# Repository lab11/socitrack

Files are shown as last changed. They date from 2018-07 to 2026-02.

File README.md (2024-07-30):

TotTag
======

If you are interested in incorporating TotTag devices into your future
research, please fill out this [Interest Form](https://forms.gle/SqWca9DrKpcx9rBL6).

> **Note: This system is currently under heavy development. At the moment, it
> is provided as-is with no mechanism for external support, technical or
> otherwise.  In the future, once the project has reached a steady state and
> staffing has ramped up, we may begin providing limited support. We will post
> any updates on that front here. Thank you for your understanding!**

The TotTag is a self-contained PCB which utilizes a hybrid ultra wideband (UWB)
and Bluetooth Low Energy (BLE) radio design to enable high-fidelity interaction
tracking between devices _without_ requiring any supporting infrastructure.

<!--
- The SquarePoint module - 3 UWB antennas
- Nordic Semiconductors nRF52840 BLE radio
- 3.3V LDO designed to be used with 4.2V LiPo batteries
- Battery charge management controller
- SD card holder
- microUSB connector including FTDI FT232R for debugging
- 3-axis accelerometer
-->

TotTag saw a major plaform refresh in 2023 with a largely new hardware and
software design. Please bear with us as documentation and guidance throughout
this repositority updates to match the latest state of the TotTag project.

- [Documentation & Getting Started Guide](doc/)
- [Hardware details](hardware/)
- [Software details](software/)

History, Related Projects, & Relevant Publications
==================================================

This current effort builds on a long line of work exploring the capabilities of
ultra wideband under resource-constrained settings. This repository is an
evolution of projects exploring COTS-based solutions; some others linked below
explore more custom ultra wideband as well.

SociTrack and TotTag Gen 1
--------------------------

- Salo, V. C., Pannuto, P., Hedgecock, W., Biri, A., Russo, D. A., Piersiak, H. A., & Humphreys, K. L. (2022). Measuring naturalistic proximity as a window into caregiver-child interaction patterns. Behavior research methods, 54(4), 1580–1594. https://doi.org/10.3758/s13428-021-01681-8

- Andreas Biri, Neal Jackson, Lothar Thiele, Pat Pannuto, and Prabal Dutta. 2020.
*SociTrack: Infrastructure-Free Interaction Tracking through Mobile Sensor Networks.*
In The 26th Annual International Conference on Mobile Computing and Networking
(MobiCom ’20), September 21–25, 2020, London, United Kingdom. ACM, New York, NY,
USA, 14 pages. https://doi.org/10.1145/3372224.3419190

<!--
- Andreas Biri, Pat Pannuto, and Prabal Dutta. 2019.
*Demo Abstract: Tot-Ternary - A Wearable Platform for Social Interaction Tracking.*
In The 18th International Conference on Information Processing in Sensor Networks
(co-located with CPS-IoT Week 2019) (IPSN ’19), April 16-18, 2019, Montreal, QC,
Canada. ACM, New York, NY, USA, 2 pages. https://doi.org/10.1145/3302506.3312486
-->

<details>
<summary>Legacy documentation from SociTrack / TotTag Gen 1
</summary>

SociTrack
=========

*SociTrack* is a system for using ultra-wideband RF time-of-flight processing to
perform indoor ranging and localization. It incorporates the *SquarePoint*
module, containing a DecaWave DW1000 radio for UWB packet transmission and
timestamping. This module provides node-to-node ranges over an I<sup>2</sup>C
interface which can then be stored locally or transmitted externally.

Hardware
--------

The **SociTrack** system is composed of several hardware pieces. At its core is
the *SquarePoint* module, a 30mm x 15mm PCB that encompasses all of the
core ranging hardware and firmware. *SquarePoint* is provided as an EAGLE board
that allows for direct integration as a design block as part of the
[Lab11 EAGLE library](https://github.com/lab11/eagle). One example of a project
that uses the *SquarePoint* module is the *TotTag*, which comprises an
all-in-one tracking and localization system for mobile nodes. The *TotTag*
hardware includes three UWB antennas and a Bluetooth Low Energy (BLE) radio,
plus a battery charging circuit, SD card for data logging, accelerometer, USB
connectivity, and integrated sensor fusion. TotTag is able to provide ranges and
position estimates directly to a mobile phone application in real-time and can
be configured on-the-fly using a simple user interface over
[Summon](https://github.com/lab11/summon).

### SquarePoint

SquarePoint, an EAGLE design block for UWB ranging, includes the following
components:

- DecaWave DW1000 UWB radio
- STMicroelectronics STM32F091CCU6 MCU
- RF switch

The MCU contains all of the necessary code to control the DW1000 and run the
ranging protocol. This module provides a simple abstraction layer for quick
integration with a carrier board over an I<sup>2</sup>C interface without having
to worry about any underlying implementation details.

### TotTag

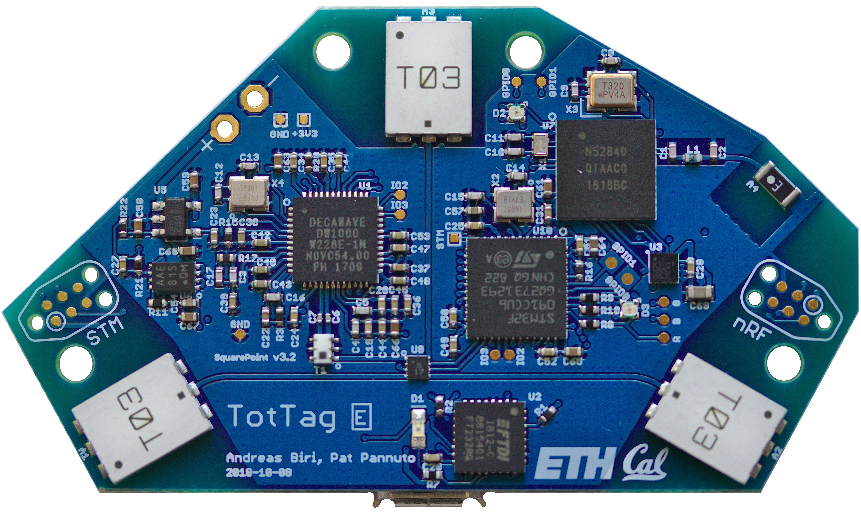
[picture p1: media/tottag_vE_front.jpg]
TotTag Front


The TotTag is a self-contained PCB which utilizes SquarePoint to provide ranging
data for human interaction tracking. It includes:

- The SquarePoint module - 3 UWB antennas
- Nordic Semiconductors nRF52840 BLE radio
- 3.3V LDO designed to be used with 4.2V LiPo batteries
- Battery charge management controller
- SD card holder
- microUSB connector including FTDI FT232R for debugging
- 3-axis accelerometer

The TotTag is designed to be a device that can be used as a ranging anchor, a
mobile tag, or a hybrid combination of both. It offers both infrastructure-free
and infrastructure-based network processing and allows for centimeter-accurate,
multi-day deployments. Both the schematic and board design are open-source and
can be found in the [`hardware/tottag`](hardware/tottag) folder; a suitable 3D
printable case is also provided in
[`hardware/cad/tottag-case`](hardware/cad/tottag-case/).

Software
--------

The SociTrack software is freely available as an open-source Git repository.
When cloning this repository, be sure to do

    git clone --recursive https://github.com/lab11/socitrack.git

or to later run

    git submodule init && git submodule sync

so that all submodules are cloned as well. All of the supporting libraries and
build tools are in submodules for the various hardware platforms used in this
project.

#### SquarePoint

Found in [`software/squarepoint`](software/squarepoint/), the core firmware that
enables the SquarePoint module to work includes all of the logic implementing
our custom ranging protocol on top of the DecaWave DW1000 UWB radio. It makes
use of frequency and antenna diversity and leverages both one-way and two-way
ToF ranging to achieve efficient and reliable ranging in various environments.
The firmware architecture supports multiple runtime modalities that can
be selected on-the-fly; currently, we officially support:

- *Standard*: the full ranging protocol, using maximal diversity to achieve
              highly-reliable ranging measurements over 30 different channels.
- *Calibration*: automatically triggered by our calibration scripts, allowing
                 for automated board-specific calibration functions which are
                 then applied to future ranging measurements.

#### TotTag

The TotTag code, located in [`software/tottag`](software/tottag/firmware/),
implements a BLE application that uses the SquarePoint module as an
I<sup>2</sup>C slave and provides for external BLE connectivity. It exposes BLE
services to configure and enable the device, to set the current time to enable
accurate timestamping of ranging data, as well as to access ranging data in
real-time.

#### Mobile App and BLE

The tools in the [`software/tottag/mobile_app`](software/tottag/mobile_app/)
directory interact with TotTag and read data across the BLE interface. They uses
the Summon app ([Google Play](https://play.google.com/store/apps/details?id=edu.umich.eecs.lab11.summon),
[App Store](https://itunes.apple.com/us/app/summon-lab11/id1051205682)) to
easily access and interact with the TotTag devices. The target website must be
configured in the TotTag code and can be hosted on a personal domain; we
recommend the use of a link shortener to reduce the BLE advertisement length.

### Linux Development

This project requires the [GNU ARM Embedded Toolchain](https://developer.arm.com/open-source/gnu-toolchain/gnu-rm).
Please be aware that the some Linux distros provide out-of-date versions of this
tool; as such, we strongly recommend that you install the newest version
directly from ARM.

</details>

SurePoint
---------

The original projects exploring COTS UWB technology.

PolyPoint introduced the concept of antenna diversity, and demonstrated its
efficacy by finishing as the best-performing UWB-based system at the 2015
Microsoft Indoor Localization competition.

SurePoint expanded on the PolyPoint concepts and built a complete system around
efficient channel diversity, and showed how to scale up robust ranging with
COTS UWB.

- Benjamin Kempke, Pat Pannuto, Bradford Campbell, and Prabal Dutta. 2016.
*SurePoint: Exploiting ultra wideband flooding and diversity to provide robust, scalable, high-fidelity indoor localization.*
In Proceedings of the 14th ACM Conference on Embedded Network Sensor Systems
(SenSys ’16), November 14-16, 2016, Stanford, CA, USA.  ACM, New York, NY,
USA, 13 pages. https://doi.org/10.1145/2994551.2994570

- Benjamin Kempke, Pat Pannuto, and Prabal Dutta. 2015.
*PolyPoint: Guiding indoor quadrotors with ultra-wideband localization.*
In Proceedings of the 2nd International Workshop on Hot Topics in Wireless
(HotWireless ’15), September 11, 2015, Paris, France. ACM, New York, NY,
USA, 5 pages. https://doi.org/10.1145/2799650.2799651

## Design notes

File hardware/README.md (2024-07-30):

Hardware
========

TotTag Gen 2 (2023-present)
---------------------------

- `rev_i` is a fairly complete overhaul of the TotTag platform, shedding
many of the legacy IC selections from the long design history of this project
(some traced back to the original 2015 PolyPoint board).

   - The most significant changes are moving from a dual-MCU design to a single MCU,
based around the Ambiq Apollo4 family of chips, and upgrading to the newer
generation UWB transciever, ~~Decawave~~ Qorvo's DW3000 family.

   - `rev_i` is in many ways a first revision of a new board.

- `rev_k` fixed most of the major flaws in from `rev_i`, but introduced new
problems around the DW3000.

- `rev_l` hedged around continued DW3000 issues and replaced the integrated
design with three copies of Qorvo's pre-fab module. This is a temporary
patch to get working systems with the new transciever more quickly to enable
scale-up.

- `rev_m` has only trivial, cosmetic fixes over `rev_l`.

- `rev_n` (in progress) removes the pre-fab UWB modules, and returns to the
integrated UWB design, which re-opens access to antenna diversity and the
improved robustness of ranging performance.

TotTag Gen 1 (2020-2023)
------------------------

Revisions of the original TotTags from the SociTrack project that focused on
the deployability, scaling, and robustness of the caregiver-infant interaction
tracking application.

This resulted in a more tightly integrated design as well as one more
aggressively geared towards a "wireless only" approach to ease device
management at-scale.

For more details, see the documentation in the [tottag folder](tottag/).

SociTrack (and TotTag Gen 0) (2017-2020)
----------------------------------------

The SociTrack system consists of a single PCB which integrates both an
application board and a SquarePoint module. SquarePoint is available from the
[*Lab11 EAGLE* library](https://github.com/lab11/eagle) as a design block
(check version number).

The original tottags (i.e., rev_c and rev_d) follow this more modularized
design, keeping SociTrack's components as cleanly separable features, but
integrating into a single PCB dual microcontrollers and enhanced functionality
such as SD card logging, accelerometer information, USB connectivity, wireless
charging, debugging ports, and LEDs, as well as battery voltage sensing.

PolyPoint (2015) and SurePoint (2016-2017)
------------------------------------------

The PolyPoint system consists of several PCBs centered around TriPoint, the core
UWB ranging module.

1. **TriPoint**: A triangular module which contains all of the necessary hardware
for utilizing a DecaWave DW1000 UWB radio. It has castellated headers so it can
be soldered onto a carrier board to add indoor localization functionality to any
device.

2. **TriTag**: A portable carrier board designed to be used as an indoor
localization tag. Contains TriPoint on one side and a BLE radio on the other.

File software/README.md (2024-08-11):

SquarePoint Software
====================

This directory contains all software packages and solutions related to the TotTag infrastructure.

Current
-------

- [firmware](firmware/) - TotTag firmware for the current generation (Ambiq Apollo) microcontroller
- [management](management/) - Python-based GUI for management of TotTag deployments and experiments

Deprecated
----------

- [analysis](analysis/) - Scripts to perform data analysis on TotTag Generations 0 and 1 output
- [ersp](ersp/) - Tools to predict system lifetime and configure protocol parameters

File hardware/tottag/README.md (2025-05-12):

TotTag Revision History
=======================

The original localization platform was developed by the Lab11 research group,
primarily by @bpkempke, @bradjc, and @ppannuto.

The original TotTag hardware (rev_c, rev_d) was developed @abiri during his
Master's Thesis work when he was a visiting scholar with the Lab11 research
group.

Current TotTag hardware is maintained by @ppannuto and @corruptbear.

## "Gen 2" TotTags

Revision I is a fairly complete hardware refresh and board redesign. Initially
necessitated by the COVID-era chip shortage, it became an opportunity to take
advantage of the next generation of low-power MCUs and radio hardware.
Revisions K, L, and M split the board into two physical modules to isolate
design challenges with some of the new chips; revision N re-integrates the
design back to a single module. Revisions O and P center on smaller fixes for
DFM and scale.

### Rev O
Highlights:
 - Connect USB data lines to enable wired offload
 - Remove long-unused hedges and debug (solder jumpers, zero-Ω, and DNP parts; SWTRACE)
 - UWB: Integrate LNA on common signal path for all antennas

[Complete list of Rev O updates](https://github.com/lab11/socitrack/issues/59)

### Rev N
[Rev N updates](https://github.com/lab11/socitrack/issues/58)
__Note: The main board is derived from Rev K, and integrates AP4BP Rev-B back on-board.__
 - Re-integrate AP4BP
    - Remove duplicate concepts (LEDs, TagConnect headers, etc)
    - Match stackup (choose module's 0.6mm for microvias; update 50Ω for all RF)
 - Update IMU to BNO086
 - Update UWB components
    - Generally update design to match new Qorvo app note APH301, bigger things...
       - Revise layout of power rails
       - Update via fencing spacing to lambda/20
       - Remove soldermask from transmission lines
    - Switch from DW3210 (QFN) to DW3110 (WLCSP aka BGA)
       - WCSNG group reports BGA more reliable part
       - Next-gen part QM33110W [released; no stock; pin compatible; update when able] is BGA only
    - Revert from TCXO to XTAL (new rec'd components available)
    - Update key passives to 0603 C0G Low-ESL variants
    - Add Qorvo LNA
       - This rev hedges and only adds to RF1 trace; later rev will move to RFC if fruitful
       - This rev does not add optional band-pass filter
       - Also adds VR3, another copy of the low-noise LDO
  - DFM work
    - Shrink top-metal traces on AP4 BGA perimeter to 5 mil to better match trace 75% of ball pad diameter guidance
    - Add dedicated clean areas for mouse bite tabs
    - Update some passives to Worthington's "ideal" smd component footprint
    - Swap IOM's for DW and 9DOF to ease routing
    - Remove most microvias not on BGA pads

### Rev M + AP4BP Rev-B
[Rev L Issues / Rev M updates](https://github.com/lab11/socitrack/issues/49)
 - Fix silkscreen error on switch label

### Rev L + AP4BP Rev-B
[Prior rev's issues / updates](https://github.com/lab11/socitrack/issues/46)
 - Fixes first-rev issues from the AP4BP module.
 - Rips out our UWB in favor of DWM3000 pre-fab modules for Qorvo as a hedge
   to facilitate more certain-to-work UWB in the short term (but sacrificing
   diversity and robustness [and adding cost]).

### Rev K + AP4BP Rev-A
[Rev I Issues / Rev K Updates](https://github.com/lab11/socitrack/issues/44)
 - (n.b., there is no Rev J to avoid I/J confusion)
 - Move to Apollo4 Blue Plus (Blue has too many silicon bugs)
    - Split this to a castellated module for separation of hw design concerns
 - Move to TCXO for DW3000 (bad idea; will be removed next rev)

### Rev I ***(Major Revision)***
 - Refresh part selection to replace 2015 parts with improved modern versions
 - Major change: Apollo4 Blue as sole MCU
 - Major change: DW3000 replaces DW1000 as UWB transceiver
 - Really, most stuff changed except the wireless charging

## "Gen 1" TotTags

Revisions C–H mark the first generation of TotTag hardware, i.e., that designed
primarily as hardare for social interaction tracking. Generation 1 TotTags
carry a lot of design decisions from the original indoor localization system,
and are generally built on "2010-2020" era technologies.

### Rev H
[Rev G Issues / Rev H Updates](https://github.com/lab11/socitrack/issues/9)
 - Isolates high-bandwidth accelerometer to dedicated SPI bus
 - Revises wireless charging design for robustness
 - Resolve RTC design issues
 - DFM cleanups

### Rev G
[Rev F Issues / Rev G Updates](https://github.com/lab11/totternary/issues/7)
 - Add detachable battery connector
 - Add power switch
 - Adapt PCB shape for mass-production case

### Rev F

[Rev E Issues / Rev F Updates.](https://github.com/lab11/totternary/issues/4)
 - Add RTC

### Rev E

[Rev D Issues / Rev E Updates.](https://github.com/lab11/totternary/issues/3)

Rev E updates:
 - Major performance improvements
   - Revise routing, part layout to improve RF performance
   - Capacitor layout around nRF to fix crystal stability issues
 - Add optional switching regulator bypass

### Rev D

[Rev D Issue.](https://github.com/lab11/totternary/issues/2)

Rev D updates:
 - Add low battery indication
 - Testpoints for buses
 - Fix reset signal for nRF52840
 - Several PCB improvements

### Rev C

[Rev C](../../tritag/rev_c/)

Revision C was the first of the 'tottag' family of revisions (though not yet
named as such). It converted the previous hardware modularity into Eagle design
blocks, and was the first single-board revision. It added several features
(storage, sensors) that were not part of the tritag design.

Rev C Major Highlights:
  - Modularize (design block) ranging design
  - Update BLE to nRF52840
  - Add SD Card
  - Add Accelerometer
  - Update charging design
  - Integrate FTDI

## Older revisions

Prior iterations of this platform were developed for the "Polypoint" project,
which later became the "Surepoint" project.

The tottag hardware is largely an evolution of the
[tritag](https://github.com/lab11/polypoint/tree/master/pcb/tritag) module
from these projects.

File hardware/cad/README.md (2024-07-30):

CAD Models
==========

A few designs of various cases and mounts used for different iterations of
hardware over the course of this project.

---------------------------------------------------------------------------

**Note:** As of this writing (July 2024), none of these designs are relevant to
the recent generations of TotTag PCBs. For the last few years, the board has
been designed to fit in the OKW Minitec case, specifically the
[B9006856](https://www.okwenclosures.com/en/Minitec/B9006856.htm).
You will also need the plastic ring which sits between the two halves of the
case, e.g. [B9006782](https://www.okwenclosures.com/en/Minitec/B9006782.htm)
(n.b., color doesn't affect anything; our original order bought 30 cases and 5
each of B9006782-B9006888).

**If you will be opening and closing the cases often,** we had OKW install
metal receptacles in the posts for the screws in our larger order. This widens
the plastic post width slightly (the PCB does not rely on the screw posts for
alignment or mounting in either case, so this should not affect things
generally). The new posts accept a `M2,5` screw. The product number for our
final case is `B9006A30`, which I believe is an internal code for the
customization they did for our design, and not a publicly available model.
However, hopefully their sales team can look up the old design by this
reference for your order if-needed, and do the same modification.

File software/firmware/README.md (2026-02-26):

TotTag Firmware
===============

This firmware is intended for use with the Ambiq Apollo4 line of microcontrollers and contains all
ranging and localization algorithms for the TotTag system.

Getting Started
---------------

To install this firmware onto a TotTag device, you will need to obtain a
[J-Link Programmer from SEGGER](https://www.segger.com/products/flasher-in-circuit-programmer/). If you are using this
product for educational or research purposes, you may be able to obtain a programmer at a significantly reduced price, such
as the [J-Link EDU Probe](https://shop-us.segger.com/product-category/debug-probes/educational/). You will also need a
set of cables to connect the programmer to the TotTag board:

* [Tag-Connect 20-pin to 10-pin IDC adapter](https://www.tag-connect.com/product/tc2050-arm2010-arm-20-pin-to-tc2050-adapter)
* [Tag-Connect 10-Pin No-Legs Plug-of-Nails™ Cable](https://www.tag-connect.com/product/tc2050-idc-nl-10-pin-no-legs-cable-with-ribbon-connector)

You will also need to install the [SEGGER J-Link Software and Documentation Pack](https://www.segger.com/downloads/jlink/)
onto your computer.

Once these items have been taken care of, you can flash the firmware onto a device using the following procedure:

1. Connect the Tag-Connect adapter and cable to the J-Link Programmer.
2. Connect one end of the J-Link Programmer to your computer via USB.
3. Connect the other end of the J-Link Programmer to the TotTag device by inserting the Tag-Connect cable into the
set of holes on the TotTag board labeled "XA2" (see image below).
4. On your computer, navigate to the root of this firmware directory (i.e., `cd socitrack/software/firmware`).
5. If this is the first time you are programming your TotTag, you will need to assign it a unique ID in the form of
`c0:98:e5:42:00:XX` where you are free to choose whichever values you would like for `XX`. Valid values for X are all
integers and all characters between 'A-F' (i.e., 2 valid IDs might be `c0:98:e5:42:00:02` or `c0:98:e5:42:00:F3`).
7. Assign your chosen ID to the TotTag by typing `make ID=c0:98:e5:42:00:XX UID` (**YOU ONLY NEED TO DO THIS ONCE**).
8. Flash the firmware onto the TotTag by entering `make flash`.
9. If everything was successful, you should hear a happy sounding chime when you place the TotTag on a wireless charger.
10. Remove all cables, close the TotTag case, and replace the screws.

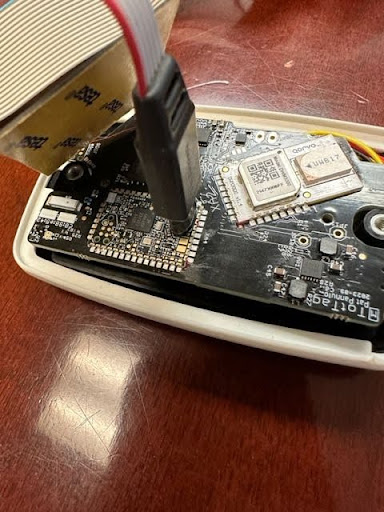
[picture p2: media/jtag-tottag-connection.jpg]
TotTag J-Link Connection


Updating the Firmware
---------------------

If you ever need to update the firmware on your TotTag, you can always obtain the latest firmware
and flash it onto your device by doing the following (**REPLACE `BOARD_REV=X` WITH THE REVISION OF THE BOARD YOU ARE FLASHING**):

```
cd socitrack
git pull
cd software/firmware
make clean
make BOARD_REV=P flash
```

It is important to watch the end of the output whenever flashing the firmware to your device.
A lot of text will fly by, but near the end you should see:

```
Downloading file [bin/SociTrack.bin]...
Comparing flash   [100%] Done.
Erasing flash     [100%] Done.
Programming flash [100%] Done.
Verifying flash   [100%] Done.
```

Or possibly just:

```
Downloading file [bin/SociTrack.bin]...
Comparing flash   [100%] Done.
```

The second case will happen if the device was already programmed correctly.

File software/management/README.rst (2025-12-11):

TotTag Management Dashboard
===========================

Overview
--------

This directory contains all source code for the TotTag Management Dashboard. All setup and preparation for live pilot testing should be carried out through the TotTag Dashboard.

Installation
------------

The easiest way to install this tool is through `pip` by entering:

``python3 -m pip install tottag``

If you wish to install the package manually or develop it further, you should first clone the `SociTrack repository <https://github.com/lab11/socitrack>`_ to
your hard drive, `cd` into the ``software/management`` directory, then issue the following command in a terminal:

``python3 -m pip install -e .``

Usage
-----

Once installed, the management dashboard is accessible from any terminal by entering the following command:

``tottag``

You do not need to navigate to the SociTrack source code directory to run the application.

Usage of the TotTag Dashboard should be relatively straightforward, keeping in mind a few caveats:

•	A TotTag device is only discoverable and visible if it is currently being charged. If the device is not on a charger, it will not appear in the TotTag Dashboard.
•	You will not be able to carry out any management functionality unless you are actively connected to a TotTag, so if the action buttons are grayed out, ensure that you are actually connected to a device.
•	If, at any time, the application freezes or becomes unresponsive, you can always force it to close by returning to the terminal in which you entered the “tottag” command and simultaneously pressing CTRL+C. This should cause the application to forcefully terminate.

The suggested procedure for setting up a pilot deployment is the following:

1.	Determine exactly how many TotTags will be needed for the deployment, and choose this number of devices to set aside.
2.	Make a note on a piece of scratch paper about which Device IDs should be associated with which user-friendly labels.
3.	Open the TotTag Dashboard and go to the “Deployment” tab. Do not connect to any TotTags at this time.
4.	Enter all relevant information about the upcoming deployment, including the mapping of TotTag labels to Device IDs.
5.	Once all information has been entered, ensure that all relevant TotTags are discoverable in the device bar at the top of the dashboard.
6.	Click the “Start” button to start the deployment programming process for all relevant devices.
7.	Once complete, it is a good idea to individually connect to each of the participating devices and verify that both the current time and the experiment details are correct.

After the above steps have been completed, your devices are ready for shipment and will automatically shut down until time for the deployment to begin. Upon completion of a pilot test, the first thing you should do upon receipt of the TotTags is to download all log files before putting the TotTags back into storage.

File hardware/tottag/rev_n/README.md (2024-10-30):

Rev N
=====

Draft export, not yet finalized or fab'd

Fabrication Notes
-----------------

> n.b., the .brd file is the authority, this is a convenience copy of the text
> from the .brd file.

### Stackup

Designed for CircuitHub Std Fab: 4-Layer, 0.6mm

    Order   Name    Matrl   Dscrpt  Dielec  Thk(mm) CuWgt(oz)
      1:    Top     Copper  Signal          0.035   1oz
                    2116    Prepreg 4.5     0.12
      2:    Route2  Copper  Ground          0.035   1oz
                    FR4     Core    4.6     0.23
      3:    Route15 Copper  Pwr/Gnd         0.12    1oz
                    2116    Prepreg 4.5     0.12
      4:    Bottom  Copper  Sig/Gnd         0.035   1oz

### Impedence Control

50Ω for Ultra Wideband RF [5~8 GHz]
 - Controlled traces run from U2-S2-{-U7-A1,-A2,-S4-A3}
 — UWB traces are priority signals

50Ω for Ultra Wideband XTal [38.4 MHz]
 - Controlled traces run from U2-X4-{C3, C4}

50Ω for Bluetooh RF [2.4 GHz]
 - Controlled traces run from U1-L7-L8-A4

All modeled as Coplanar waveguide.

    SaturnPCB Calculator Configuration:
     Conductor Width  = 0.22 mm (8.7 mil)
     Conductor Height = 0.12 mm (4.7 mil)
     Conductor Gap    = 0.15 mm (5.9 mil)
     Er               = 4.5
     [W/H=1.836 < 2, √]
     Modeled Z        = 49.94 Ω

### Panelization

Any OK.
OK to leave mouse bite tabs any edge.
Designated tab areas are suggestions only, and have no parts or traces.

### BGAs and Vias

Parts U1 and U2 are BGAs with 4mm micro vias in pads.
Okay to plug any/all vias in design.
Okay to tent any/all vias in design [should already be tented].

### Silkscreen

Some legacy parts have silk outlines very close to copper.
Okay to crop/cut silk aggressively as-needed.

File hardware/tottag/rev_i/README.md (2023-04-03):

Rev i
=====

This is now stored in the Fusion Cloud (sigh), with their "version control"
(double sigh).

This is a one-off export of the state of the project when shipped to
manufacture, as well as the design files from CircuitHub (CM making boards).

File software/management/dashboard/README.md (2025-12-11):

# Dashboard & Processing

## Timezone interpretation

- The timestamps stored in the processed log files (the `.pkl` files) are utc timestamps.
- The plotting functions in `processing.py` plots the time series according to the local timezone of the computer running the script. If you run the same script with the same file on computers from different timezones, the plot will look different. 

## Dashboard

The TotTag dashboard is a GUI for interacting with the tags.

To bring up the dashboard without installing it first, enter:
```bash
python3 tottag.py
```

If the dashboard has been installed, you can access it anywhere by entering:
```bash
tottag
```

### Disconnected state
To discover the devices, click the scan button.

To schedule a new experiment for a group of devices, the devices have to be placed on chargers, otherwise they will not be discovered by scanning.

Once a deployment is scheduled, the schedule will be push to all devices.

### Connected state

Each device can be connected to individually.

In the connected state, any updates to the deployment only apply to the current connected device. 

To download the logs, the connected device  **needs to be on the charger**.

To view live ranging data, the connected device **should not be not on the charger**.

## Processing

### Statistics

```python
from processing import *

# load the logs
A = load_data("E1.pkl")
B = load_data("Pat.pkl")
C = load_data("SB.pkl")

# 3.0 is the touching distance threshold (could be modified)
# the unit could be 'ft' or 'm'
get_daily_ranging_statistics(A, ["Pat","SB"], 3.0, unit='ft')
get_daily_ranging_statistics(B, ["E1","SB"], 3.0, unit='ft')
get_daily_ranging_statistics(C, ["E1","Pat"], 3.0, unit='ft')
```

### Plots
```python
from processing import *
A = load_data("07.pkl")
B = load_data("09.pkl")

# plot the voltages
get_voltage_time_series(A, "07")
get_voltage_time_series(B, "09")

# plot the ranges
get_ranging_time_series(A, "07","09")
get_ranging_time_series(B, "09","07")

get_motion_time_series(A, "07")
get_motion_time_series(B, "09")
```

### Get the on and off charger time
```python
from processing import *
A = load_data("12043_S1.pkl")
get_off_and_on_charger_times(A,"10043_S1",visualize=False)

# to show the marking on the voltage plot
get_off_and_on_charger_times(A,"10043_S1",visualize=True)
```

### Visualizing paired logs with alignment

To visualize events, an event log needs to be prepared. The event log have to follow the following format
 - A single line (no `ENTER`/`RETURN` within the line) per event.
 - For each line, always start with the Y-m-d H:i:s timestamp.

```
2024-04-01 08:33:11 SB enters the room. E1 is propped up on the window sill. Pat is laying flat on the table. 
2024-02-01 08:34:58 SB leaves the room. 
```

```python
from processing import *

# load the logs
A = load_data("E1.pkl")
B = load_data("Pat.pkl")
C = load_data("SB.pkl")

# visualize paired logs
visualize_ranging_pair_slider(A,B,"E1","Pat")
visualize_ranging_pair_slider(A,C,"E1","SB")
visualize_ranging_pair_slider(B,C,"Pat","SB")

# extract events from the event log
events  = extract_simple_event_log("annotation_pst.txt")

# visualize the events
visualize_ranging_pair_slider(A,B,"E1","Pat", events=events)
visualize_ranging_pair_slider(A,C,"E1","SB", events=events)
visualize_ranging_pair_slider(B,C,"Pat","SB", events=events)

# visualize the events within [start_timestamp, end_timestamp]
visualize_ranging_pair_slider(A,B,"E1","Pat", events=events, start_timestamp=1708619580, end_timestamp=1708623540)
visualize_ranging_pair_slider(A,C,"E1","SB", events=events, start_timestamp=1708619580, end_timestamp=1708623540)
visualize_ranging_pair_slider(B,C,"Pat","SB", events=events, start_timestamp=1708619580, end_timestamp=1708623540)
```

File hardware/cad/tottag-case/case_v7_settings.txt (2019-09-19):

Application version: 2.6.2.0
Estimated print time: 5h 4m
Material usage: 11.55m (29g)
Printer: Zortrax M300
Profile: Last settings
Material: Z-HIPS
Layer: 0.09 mm
Quality: High
Infill: 90%
Fan speed: Auto
Seam: Normal
Outer contours: 0.00
Holes: 0.00
Surface layers Top: 8
Surface layers Bottom: 4
Support Lite: No
Smart bridges: No

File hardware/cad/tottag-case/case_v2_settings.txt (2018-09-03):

Application version: 2.6.2.0
Estimated print time: 3h 1m
Material usage: 8.82m (22g)
Printer: Zortrax M300
Profile: Last settings
Material: Z-HIPS
Layer: 0.14 mm
Quality: High
Infill: 90%
Fan speed: Auto
Seam: Random
Outer contours: 0.00
Holes: 0.00
Surface layers Top: 8
Surface layers Bottom: 4
Support Lite: No
Smart bridges: No

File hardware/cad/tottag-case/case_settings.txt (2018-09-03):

Application version: 2.6.2.0
Estimated print time: 2h 57m
Material usage: 8.76m (22g)
Printer: Zortrax M300
Profile: Last settings
Material: Z-HIPS
Layer: 0.14 mm
Quality: High
Infill: 90%
Fan speed: Auto
Seam: Random
Outer contours: 0.00
Holes: 0.00
Surface layers Top: 5
Surface layers Bottom: 5
Support Lite: No
Smart bridges: No

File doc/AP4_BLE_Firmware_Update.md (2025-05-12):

## BLE firmware update method

1. Navigating to the folder in the AmbiqSuite SDK which contains the firmware update example

```bash
# adjusting the path if neccesary
cd AmbiqSuite_R4.5.0/AmbiqSuite_R4.5.0/boards/apollo4p_blue_kbr_evb/examples/ble/ble_firmware_update/gcc
```

2. Run the following commands, with JLink debugger attached to the device.
```bash
make

echo 'r
loadfile bin/ble_firmware_update.bin 0x00018000
r
g
exit' > bin/flash.jlink

JLinkExe -device AMA4B2KK-KBR -if swd -speed 4000 bin/flash.jlink
```

3. Reflash the device with the app, and verify the updated firmware version at device startup.
```
Reset Reasons: HW Power-On Reset, 
BLE Controller Info:
        SBL Ver:     V1
        FW Ver:      1.22.0.0
        Chip ID0:    0x92492492
        Chip ID1:    0x4170383c
```

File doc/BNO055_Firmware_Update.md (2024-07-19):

## update procedure

Before updating BNO055 firmware via the `9DOF Debug` debugging interface, the Ambiq chip should be flashed with a firmware (such as `test_buzzer.c`) that does not activate BNO055, otherwise the JLink connection would not be established.

```bash
#start JLink 
JLinkExe -Device ATSAMD20J18A -if SWD -speed 4000 -AutoConnect 1

#inside JLink program
#this load the new firmware, not including the bootloader
loadbin mybno.bin 0x4000

```

## save older firmware
using a normal tottag, with JLink connection established
you can save the original bootloader or the firmware, just incase something goes wrong

```
savebin bl.bin 0x0000 0x4000 //save the bootloader, from start up to address 0x4000
savebin saved.bin 0x4000 0x3C000 //save the firmware, not including the bootloader
savebin full.bin 0x0000 0x3c00 //save the full firmware, including the bootloader
```

on a trial device, load the saved firmware

```
loadfile saved.bin 0x4000
```

the bno055 bootloader could also be obtained from
https://github.com/NightHawk32/BMF055-flight-controller/blob/master/AT04189_bootloader/load%20sam-ba/samd20_sam-ba_image.hex

## restore bricked bno055 using openocd

with a bricked device, the i2c read in `imu_init` fails

in this case, [openocd](https://openocd.org/pages/getting-openocd.html) could be used.

```bash
#tab 1: connect to the device
openocd -f interface/jlink.cfg -c "transport select swd"  -f target/at91samdXX.cfg -c

#tab 2: tell the device to unlock
telnet localhost 4444

#inside the telnet connection
#this command unlock the protected memory
at91samd bootloader 0 
```

after unlocking the protected memory, use jlink to load the original bootloader
```
loadbin bl.bin 0x0000
```

or load the full saved firmware including the bootloader
```
loadbin full.bin 0x0000
```

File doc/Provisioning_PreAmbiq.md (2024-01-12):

Provisioning
============

Every TotTag has two microcontrollers that must be programmed. In addition, each
new revision of the board hardware needs to be calibrated to ensure high-accuracy
ranging using the Ultra Wideband Radio.

If you are using an existing TotTag or have printed your own circuit board using
the designs and schematics in this repository, you should not need to perform any
further calibrations. If you are using the TotTag infrastructure in your own
design, however, you will need to carry out the calibration procedure or you may
experience a systemic absolute range offset on the order of half a meter or more.

This document will explain how to program the board microcontrollers, perform
calibration, and carry out device debugging:

- [Programming the nRF Microcontroller](#programming-the-nrf-microcontroller)
- [Programming the STM Microcontroller](#programming-the-stm-microcontroller)
- [Testing Basic Operation](#test-basic-operation)
- [Calibration](#calibration)
- [Debugging](#debugging)

## Checkout the firmware before revision H
This guide is for TotTag hardware up to revision H. You need to checkout the older firmware as the latest firmware is no longer designed for STM32 + nRF TotTag.

```bash
git checkout 67cdde4991d016ee61d7ed7892941ad19e543c95
```

To ensure that the submodules are downloaded, you might need to run

```bash
git submodule update --init --recursive
```

## Programming the nRF Microcontroller

This guide covers the step-by-step requirements necessary to program the nRF
microcontroller. If you are doing development work, there is more information in
the [TotTag README](../software/tottag/firmware).

1. Connect the JLink programmer to the nRF programming header:

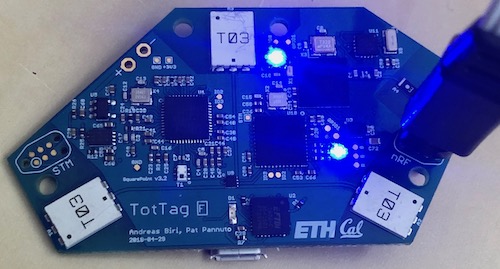
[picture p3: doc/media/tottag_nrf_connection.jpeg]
Programmer plugged into nRF side
   

   Do not worry about the LEDs at this stage, they will be random as the boards
   are not yet programmed.

2. Navigate to the [SociTrack root folder](..):

        cd socitrack

3. Ensure the repository is up to date with latest software:

        git pull --recurse-submodules
        git status
        # On branch master
        # Your branch is up to date with 'origin/master'.

4. Go to the [TotTag folder](../software/tottag):

        cd socitrack/software/tottag

5. Clean up any old build artifacts:

        make clean

6. Build the TotTag firmware. You will need the JLink serial number (`S/N` on
   the back of the JLink) and optionally, the TotTag Device ID
   (sticker on the back of the TotTag):

        make SEGGER_SERIAL=<segger_id> flash

   or to specify the Device ID (should only be done the first time the TotTag
   is being programmed):

        make SEGGER_SERIAL=<segger_id> ID=c0:98:e5:42:00:01 flash

   It is important to watch the end of the output. A lot of text will fly by,
   but near the end you should see:

        Downloading file [_build/node_sdk15_s140.hex]...
        Comparing flash   [100%] Done.
        Erasing flash     [100%] Done.
        Programming flash [100%] Done.
        Verifying flash   [100%] Done.

   Or possibly just:

        Downloading file [_build/node_sdk15_s140.hex]...
        Comparing flash   [100%] Done.

   The second case will happen if the device was already programmed correctly.

   If you are flashing the firmware for use in a debugging or development
   environment, append the flag `DEBUG_MODE=1` to the make command to enable
   certain debugging tasks and device checks:

        make SEGGER_SERIAL=<segger_id> DEBUG_MODE=1 flash

   Having problems? Check the [JLink FAQs.](./Glossary.md#miscellaneous)

## Programming the STM Microcontroller

These steps are very similar to programming the nRF microcontroller. Key
differences have been highlighted.

1. Connect the JLink programmer to the **STM programming header**.

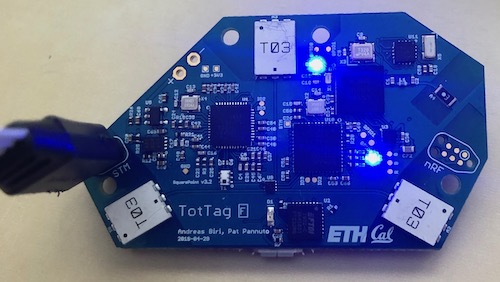
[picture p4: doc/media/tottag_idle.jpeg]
Programmer plugged into STM side
   

   Do not worry about the LEDs at this stage, they will be random as the boards
   are not yet programmed.

2. Navigate to the [SociTrack root folder](..):

        cd socitrack

3. Ensure the repository is up to date with latest software:

        git pull --recurse-submodules
        git status
        # On branch master
        # Your branch is up to date with 'origin/master'.

4. Go to the [SquarePointer folder](../software/squarepoint):

        cd socitrack/software/squarepoint

5. Clean up any old build artifacts:

        make clean

6. Build the SquarePoint firmware. You will need the JLink serial number (`S/N`
   on the back of the JLink):

        make SEGGER_SERIAL=<segger_id> flash

   It is important to watch the end of the output. A lot of text will fly by,
   but near the end you should see:

        Downloading file [_build/squarepoint.bin]...
        Comparing flash   [100%] Done.
        Erasing flash     [100%] Done.
        Programming flash [100%] Done.
        Verifying flash   [100%] Done.

   Or possibly just:

        Downloading file [_build/squarepoint.bin]...
        Comparing flash   [100%] Done.

   The second case will happen if the device was already programmed correctly.

   Having problems? Check the [JLink FAQs.](./Glossary.md#miscellaneous)

## Test basic operation

At this point, basic operation of the board should work. You will need to power
cycle the board so that both microcontrollers reset. Assuming no other tags are
nearby, both LEDs should turn solid blue:

An idle TotTag

## Calibration

**STOP. Do not perform calibration unless you have just created a new hardware
board revision. Before beginning calibration, you will need to finish the initial
setup of 3 different nodes. There is no point in setting up more than 3 nodes,
as they will all have to be reprogrammed again after calibration has completed.**

Please follow the directions in the [Calibration Documentation](../software/tottag/calibration/README.md)

Once you have finished the calibration procedure, you will need to reprogram the
nRF microcontroller for all 3 nodes you just used during calibration to ensure
they are not stuck in calibration mode. You will also need to reprogram the STM
microcontrollers on these same nodes to ensure they make use of the new
calibration data.

# Debugging

To verify that the nodes are working, you can connect two JLink programmers to
the board, one for each programming header (see above). Then, open up four
terminal windows, and enter the following commands *in order*. First, you will
connect to the STM microcontroller by entering the following (replace
`XXXXXXXXX` with the serial number of the JLink connected to the STM header,
and replace the `JLinkExe` command with `JLink` on Windows):

    Terminal 1: $    JLinkExe -Device STM32F091CC -if SWD -speed 4000 -RTTTelnetPort 9200 -SelectEmuBySN XXXXXXXXX

    Terminal 2: $    telnet localhost 9200

Do the same thing now for the nRF, whereby you enter the serial number of the
*second* JLink programmer for `XXXXXXXXX`:

    Terminal 3: $    JLinkExe -Device NRF52840_XXAA -if SWD -speed 4000 -RTTTelnetPort 9201 -SelectEmuBySN XXXXXXXXX

    Terminal 4: $    telnet localhost 9201

You can now connect to the microcontrollers and start producing output:

    Terminal 1: $    J-Link>connect
                     J-Link>r

    Terminal 3: $    J-Link>connect
                     J-Link>r

Now that you have successfully connected to both of the chips and reset them
(using the second `r` command), it is time to execute the programs. To do so,
**first start the STM and thereafter the nRF**:

    Terminal 1: $    J-Link>g

    <-- AFTER starting the STM in Terminal 1, you can then execute the command below in Terminal 3 to start the nRF -->

    Terminal 3: $    J-Link>g

Now, you should observe the startup debug output in the corresponding terminals
2 and 4:

    Terminal 2: $    ----------------------------------------------
                     INFO: Initialized RTT...
                     INFO: Successfully loaded calibration values with EUI XX
                     INFO: Connecting to host interface...
                     [...]

    Terminal 4: $    ----------------------------------------------
                     INFO: Initializing nRF...
                     INFO: Initialized software modules
                     [...]

In case you would like to restart the chips, simply enter `r` followed by `g`
in the corresponding terminals 1 and 3. Make sure to **always first restart the STM before restarting the nRF**.

To exit debugging, enter `qc` in terminals 1 and 3:

    Terminal 1: $    J-Link>qc

    Terminal 3: $    J-Link>qc

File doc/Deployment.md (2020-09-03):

Deployment
==========

Basic case deployment

_Outline_

 - SD Card protocol

 - TODO: RTC protocol

 - Battery procedures / power switch

 - While it's in the field

   - (LED good/bad/okay documentation)

 - When it comes back (SD expected behavior)
 
 - See `software/analysis/README.md` for description of how to manage
 and work with SD Card and log files

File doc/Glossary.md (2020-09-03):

Glossary
========

This document provides an overview of the TotTag infrastructure and outlines any
software or hardware you may need.

- [Hardware Glossary](#hardware-glossary)
- [Software Glossary](#software-glossary)
- [Miscellaneous](#miscellaneous)

Hardware Glossary
-----------------

These are the major pieces of the TotTag platform and supporting development
environment. You should make sure to have all of these pieces before beginning.

<table>
  <tr><th>Name</th><th>Picture</th><th>What it is used for</th></tr>
  <tr>
    <td>TotTag</td>
    <td>
      
      
    </td>
    <td>
      <p>This is the TotTag hardware.</p>
      <p>Most of the time you should not need to worry about the individual
      board components; however, it is important to pay attention to the two
      programming headers.</p>
      <p>In general, you should also avoid having large amounts of metal near
      any of the antennas.</p>
      <p><strong>Note:</strong> The Device ID is just a sticker on the board.
      When the board is programmed, you manually set the ID to match this sticker.</p>
    </td>
  </tr>
  <tr>
    <td>
      <p><a href="https://www.segger.com/products/debug-probes/j-link/models/j-link-edu/">JLink Programmer</a></p>
      <p><small>Note: This link is to the EDU edition, which should be much cheaper ($60 vs $378 at time of writing)</small></p>
    </td>
    <td>
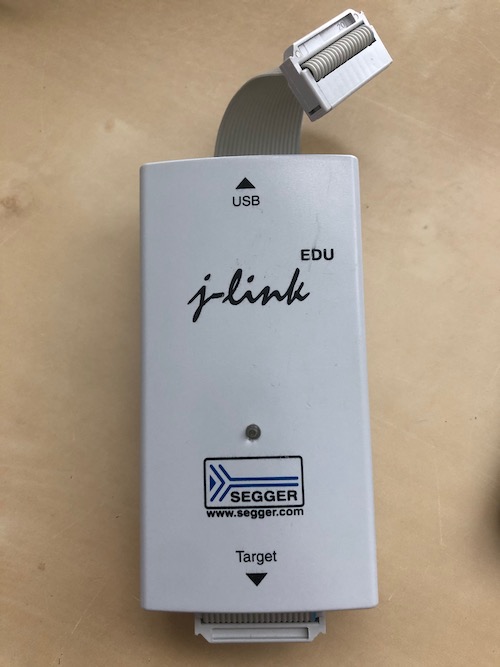
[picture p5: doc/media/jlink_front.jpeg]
      
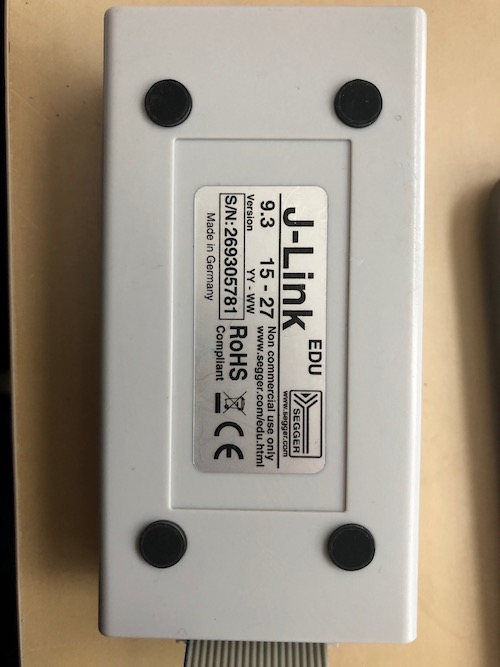
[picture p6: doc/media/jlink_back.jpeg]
      
    </td>
    <td>
      <p>This is the JLink programmer. Often just the word "Programmer" or
      "JLink" will be used, and they both refer to this device.</p>
      <p>Working with TotTags you may frequently have multiple JLinks plugged
      into your machine. On the back of each box is a serial number (the S/N
      part) that you can use to choose a specific programmer.</p>
    </td>
  </tr>
  <tr>
    <td>
      <p>JLink Adapter</p>
    </td>
    <td>
      
    </td>
    <td>
      <p>This is an adapter board designed by the Lab11 team.</p>
      <p>You can get <a href="http://www.tag-connect.com/adapters">similar
      boards</a> from Tag-Connect directly, but they do not have the power
      control or a reset button.</p>
      <p><strong>Note:</strong> For TotTag, the switch should <strong>always</strong>
      be in the unlabeled or down position (the top position says <tt>RST</tt>).
      <p><strong>Note:</strong> Pay attention to the power switch. If the tag is
      plugged into USB or attached to a battery, the switch should be in the
      <tt>DEV</tt> ("power from device") position. If the tag is only plugged
      into the programmer, it should be in the <tt>3V3</tt> ("3.3V from the
      programmer box") position.</p>
    </td>
  </tr>
  <tr>
    <td>TagConnect Cable</td>
    <td>
      <table>
        <tr>
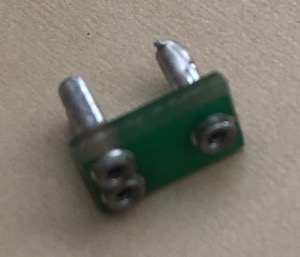
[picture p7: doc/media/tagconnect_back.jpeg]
          <td></td>
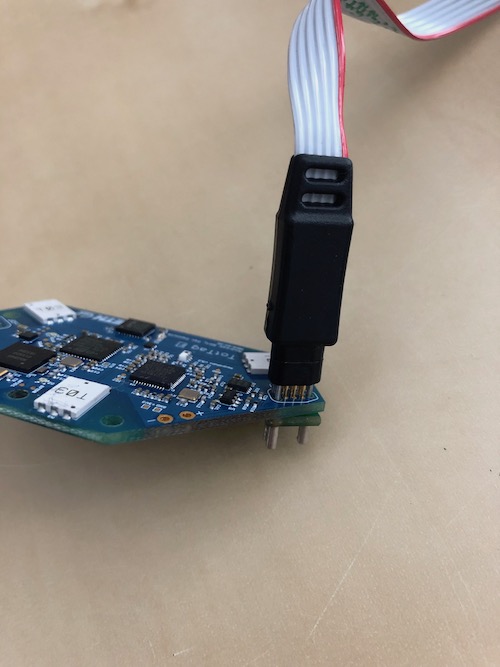
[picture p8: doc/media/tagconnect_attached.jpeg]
          <td rowspan="2"></td>
        </tr>
        <tr>
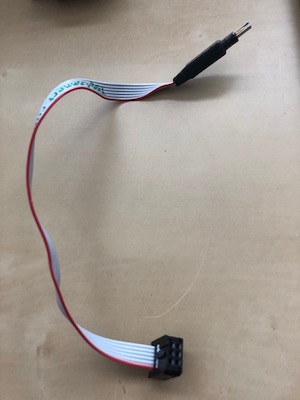
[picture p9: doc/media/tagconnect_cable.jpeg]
          <td></td>
        </tr>
      </table>
    </td>
    <td>
      <p>The <a href="http://www.tag-connect.com/TC2030-IDC-NL">Tag-Connect
      Cable</a> attaches the programmer to the board.</p>
      <p>For extended use, there is a backing board that will fix the cable
      to the board.</p>
    </td>
  </tr>
</table>

Software Glossary
-----------------

You will need to have each of these tools installed:

- [Git](https://git-scm.com/) - Version control software. Used to keep track
  of all of TotTag code and documentation.

    - **git submodule** - A method for one collection of code
    to point to another one. SociTrack uses some libraries
    that are linked as submodules. If the remote library
    updates, you will have to manually update your local
    version. Generally, this command is safe to run and will
    do everything you need: `git submodule update --init --recursive`

- [JLink Software](https://www.segger.com/downloads/jlink/#J-LinkSoftwareAndDocumentationPack) -
  Software required for your computer to talk to the JLink programmer. You need
  to press the "Click for Downloads" link under "J-Link Software and
  Documentation Pack".

Miscellaneous
-------------

 - [The SociTrack Repository](https://github.com/lab11/socitrack) - This
   website, where you will find all of the code and documentation for the
   platform.

### Debugging JLink Problems

JLink tends to fail silently or unhelpfully sometimes. Here are a few common
problems:

    J-Link connection not established yet but required for command.
    Connecting to J-Link via USB...
    # Hangs here with no more output
    
- Do you have another terminal window open that's connected to JLink (e.g. one
  with an RTT debug connection going)? You need to close that first.

- This can happen if your JLink software is older than the software on
  the JLink programmer. Every time anyone uses one of the JLink boxes, their
  software will update the firmware on the box. The JLink software prints out
  the version on your computer when it starts, but there's not an obvious way to
  see the version that's on the box. If yours is old, try updating the JLink
  software.  (As example, I ran into this problem with an old laptop running
  `SEGGER J-Link Commander V6.10c (Compiled Sep 28 2016 18:29:56)`,
  which I had to update to `SEGGER J-Link Commander V6.50a (Compiled Aug 26 2019 10:26:37)`).

- Occasionally, JLink will refuse to connect until you reboot your computer.
  I find this happens more often on Macs. No idea why.

The next step is [Setting Up a Programming Machine!](Setup.md)

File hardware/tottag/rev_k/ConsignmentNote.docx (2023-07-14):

This box contains consignment parts for TWO ORDERS.

SeaLab_Projects/00119ae5 (15615)

SeaLab_Projects/00119ae4 (15616)

One part (MCL0606FRD1GR1T) is used on BOTH ORDERS.

Please stock all excess parts at CircuitHub for future orders.

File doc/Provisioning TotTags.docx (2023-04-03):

Provisioning TotTags

General Functionality and Overview

Initial memory setup

When accessible/charging…

Initial One-Time Setup

Prior to first use, each newly manufactured TotTag must be assigned a unique Device ID in the form c0:98:e5:42:XX:XX, where the final two “XX” groupings may include any hexadecimal numbers between 00-FF. The chosen Device ID should be notated on the TotTag board itself in the designated ID label area. Once completed, the device should be connected to a battery and then flashed according to the following procedure:

1. Connect a SEGGER JTAG programming cable from your computer to the designated header on the TotTag board.
2. Open a command prompt or terminal on your computer, and navigate to the location where the SociTrack source code is stored.
3. Enter make clean to ensure that the source code directory is clean.
4. From the root directory of the source code tree, issue the following command to ensure that the latest firmware has been fetched onto your computer: git pull
5. Issue the following command to flash the TotTag with its desired ID (replacing the “XX” values with the values you annotated on the board): make ID=c0:98:e5:42:XX:XX flash
6. If the flashing was successful, there should be no error messages on your terminal, and the TotTag should make a pleasant “plugged in and charging” sound when you place it onto a wireless charger.
7. Disconnect the programming cable, and reassemble the TotTag device case. Programming is complete.

After this initial setup procedure, you should never have to reflash the device with its Device ID again.

Firmware Upgrades

If future firmware upgrades require you to reflash the device at any time, simply follow the same procedure as outlined in the previous section; however, do no include the Device ID in the flash command. Flashing is achieved by simply entering the following at a command prompt: make flash

Preparing for Live Experiments and Pilot Testing

All setup and preparation for live pilot testing should be carried out through the TotTag Dashboard application. If you have not previously used the dashboard, you must first install it by opening a command prompt, navigating to the “SociTrack/software/management” directory, and entering: python3 -m pip install

Upon successful installation of the software, you can run it by typing “tottag” in a command prompt from any location or directory. You do not need to navigate to the SociTrack source code directory to run the application.

Usage of the TotTag Dashboard should be relatively straightforward, keeping in mind a few caveats:

- A TotTag device is only discoverable and visible if it is currently being charged. If the device is not on a charger, it will not appear in the TotTag Dashboard.
- You will not be able to carry out any management functionality unless you are actively connected to a TotTag, so if the action buttons are grayed out, ensure that you are actually connected to a device.
- If, at any time, the application freezes or becomes unresponsive, you can always force it to close by returning to the terminal in which you entered the “tottag” command and simultaneously pressing CTRL+C. This should cause the application to forcefully terminate.

The suggested procedure for setting up a pilot deployment is the following:

1. Determine exactly how many TotTags will be needed for the deployment, and choose this number of devices to set aside.
2. Make a note on a piece of scratch paper about which Device IDs should be associated with which user-friendly labels.
3. Open the TotTag Dashboard and go to the “Deployment” page. Do not connect to any TotTags at this time.
4. Enter all relevant information about the upcoming deployment, including the mapping of TotTag labels to Device IDs.
5. Once all information has been entered, ensure that all relevant TotTags are discoverable in the device bar at the top of the dashboard.
6. Click the “t” button to start the deployment programming process for all relevant devices.
7. Once complete, it is a good idea to individually connect to each of the participating devices and verify that both the RTC clock and the experiment details are correct.

After the above steps have been completed, your devices are ready for shipment and will automatically shut down until time for the deployment to begin.

Upon completion of a pilot test, the first thing you should do upon receipt of the TotTags is to download all log files before putting the TotTags back into storage. TODO

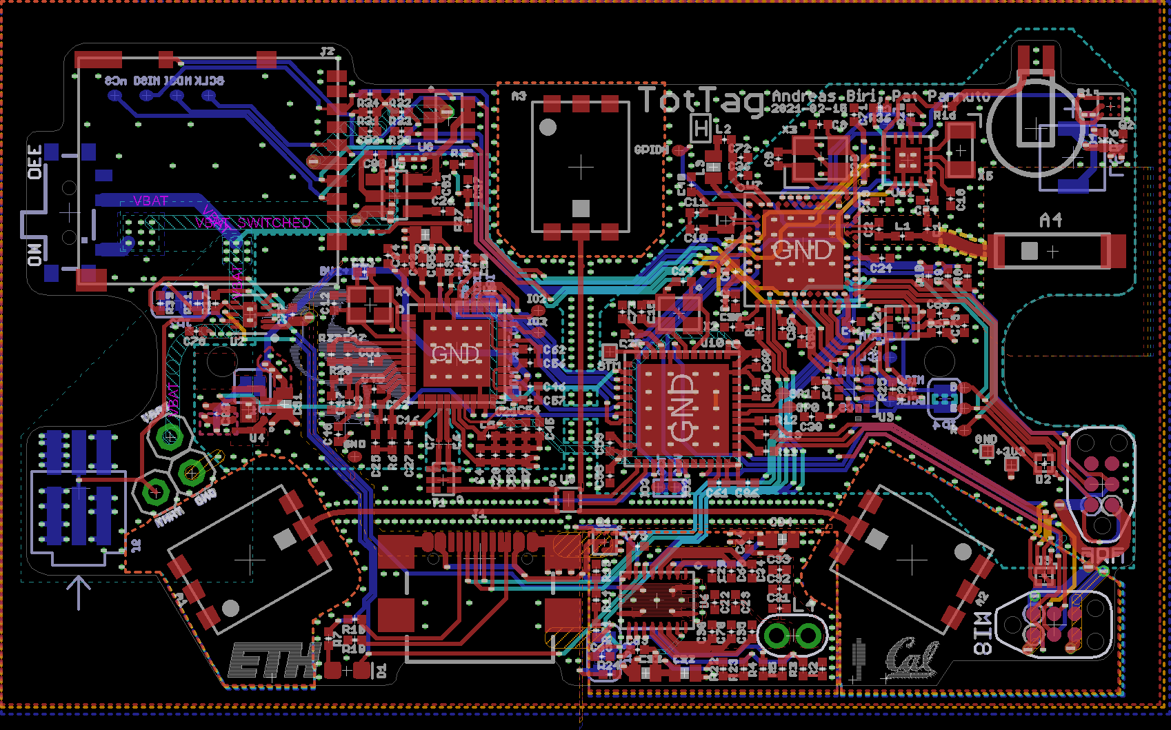
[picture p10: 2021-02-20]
hardware/tottag/rev_h/tottag_pcb.png

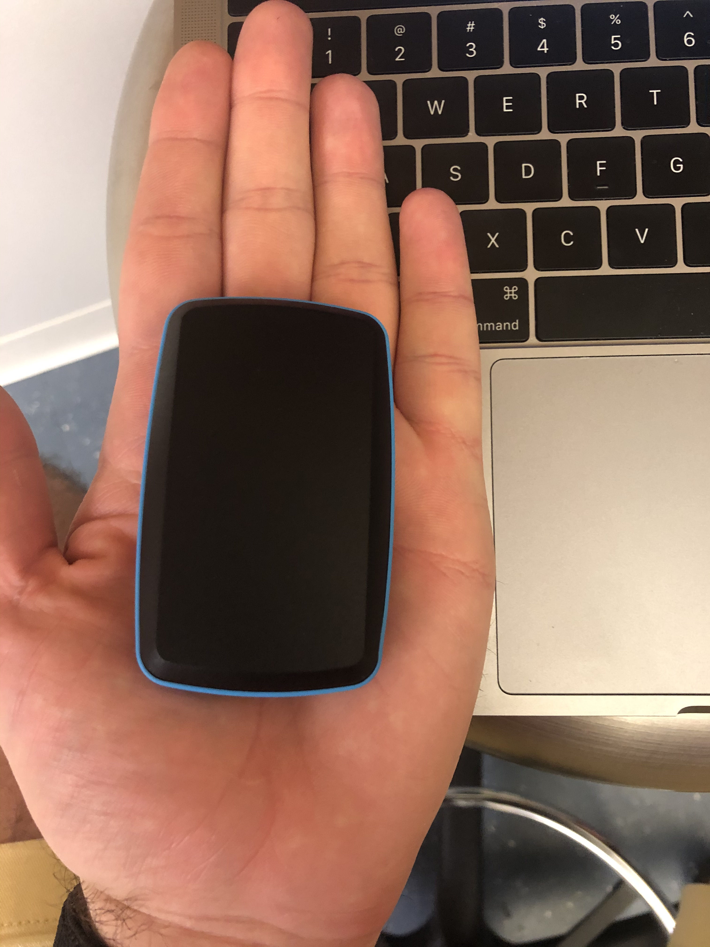
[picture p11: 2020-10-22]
media/tottag_in_hand.jpeg

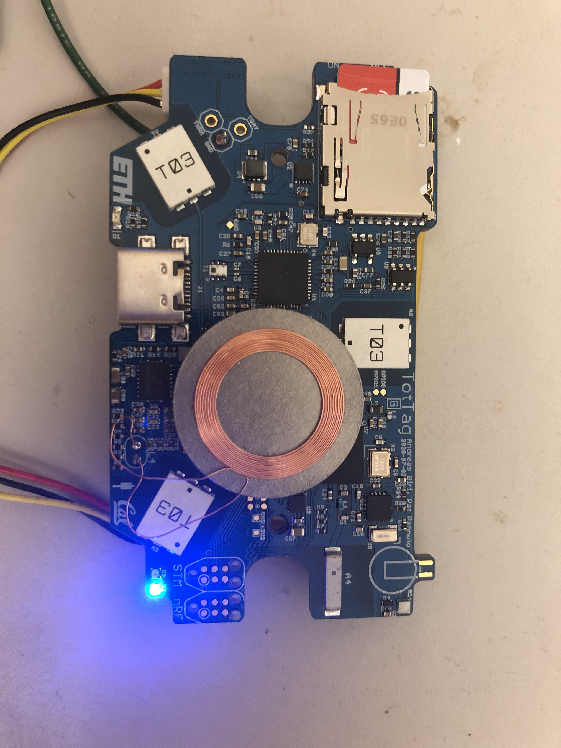
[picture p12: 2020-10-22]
media/tottag_vG_front.jpeg

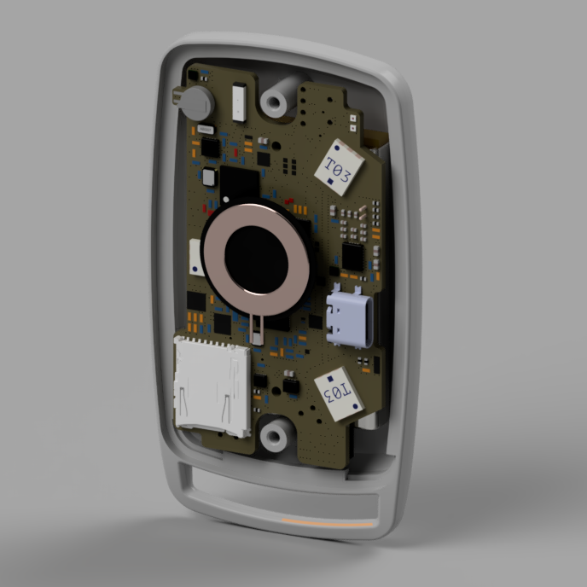
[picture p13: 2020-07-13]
media/tottag_vG_render_interior.png

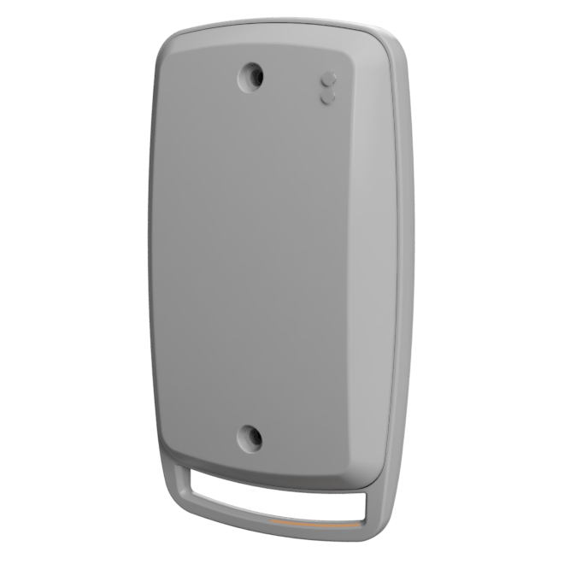
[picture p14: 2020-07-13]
media/tottag_vG_render_case.png

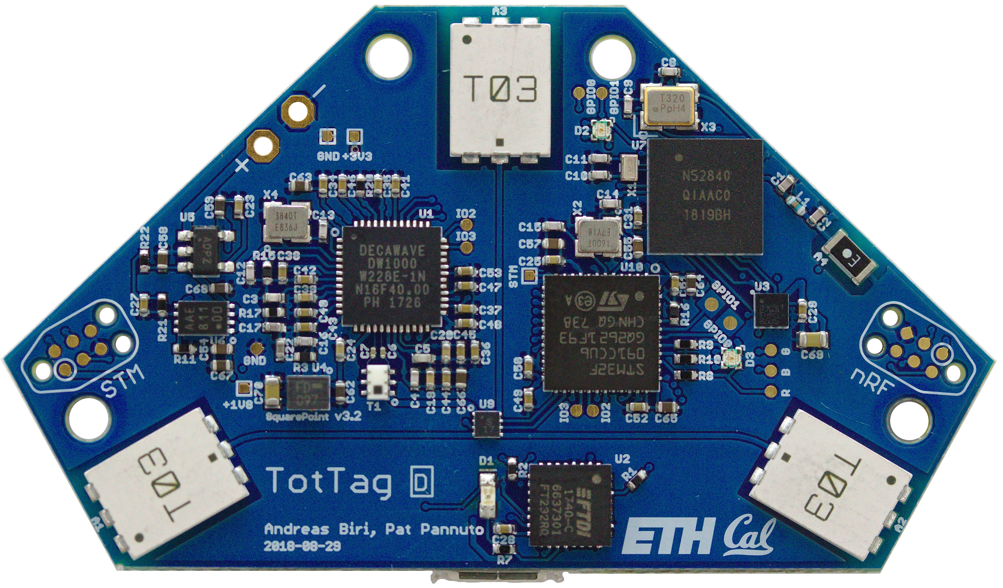
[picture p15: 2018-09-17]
media/tottag_vD_front.jpg

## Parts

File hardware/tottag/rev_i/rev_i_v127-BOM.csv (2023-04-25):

Qty | Value | Device | Package | Parts | Description | DIGIKEY | MANUFACTURER | MPN
3 | ACR0301U | ACR0301U | ACR0301U | A1, A2, A3 |  |  | Abracon | ACR0301U
1 | AMCA72-2R47G-S1F-T | AMCA72-2R47G-S1F-T | AMCA72-2R470G-S1F-T | A4 | RF ANT 2.4GHZ CHIP SOLDER SMD | 535-14108-1-ND |  | AMCA72-2R470G-S1F-T4
1 | 0.5pF | CAPACITOR0402_CAP | 0402_CAP | C1 | SMD Capacitor |  |  | GJM1555C1HR50WB01D
1 | 0.8pF | CAPACITOR0402_CAP | 0402_CAP | C2 | SMD Capacitor |  |  | GJM1555C1HR80WB01D
1 | 2pF | CAPACITOR0201_CAP | 0201_CAP | C3 | SMD Capacitor |  |  | CBR02C209A5GAC
4 | 4pF | CAPACITOR0201_CAP | 0201_CAP | C4, C5, C6, C7 | SMD Capacitor |  | Murata | GRM0335C1H4R0BA01D
2 | 6pF | CAPACITOR0201_CAP | 0201_CAP | C8, C9 | SMD Capacitor |  | Murata | GRM0335C1H6R0BA01D
2 | 12pF | CAPACITOR0402_CAP | 0402_CAP | C10, C11 | SMD Capacitor | 399-8815-2-ND |  | CBR04C120F5GAC
2 | 22pF | CAPACITOR0201_CAP | 0201_CAP | C12, C13 | SMD Capacitor |  |  | GRM0335C1H220FA01D
2 | 470pF | CAPACITOR0402_CAP | 0402_CAP | C14, C15 | SMD Capacitor | 490-6242-1-ND | Murata | GRM1555C1H471JA01J
3 | 4.7nF | CAPACITOR0402_CAP | 0402_CAP | C16, C17, C18 | SMD Capacitor |  |  | C0402C472K3RACTU
2 | 10nF | CAPACITOR0402_CAP | 0402_CAP | C19, C20 | SMD Capacitor | 490-6351-2-ND |  | GRM155R71H103KA88J
3 | 22nF | CAPACITOR0402_CAP | 0402_CAP | C21, C22, C23 | SMD Capacitor | 490-10699-2-ND |  | GRM155R71E223JA61D
2 | 22nF | CAPACITOR0402_CAP | 0402_CAP | C24, C25 | SMD Capacitor | 311-3823-1-ND |  | CC0402ZRY5V8BB223
1 | 0.1uF | CAPACITOR0201_CAP | 0201_CAP | C26 | SMD Capacitor |  |  | CL05A104KP5NNNC
4 | 0.1uF | CAPACITOR0402_CAP | 0402_CAP | C27, C28, C29, C30 | SMD Capacitor | 490-6328-1-ND |  | GRM155R71C104KA88J
9 | 0.1uF | CAPACITOR0402_CAP | 0402_CAP | C31, C32, C33, C34, C35, C36, C37, C38, C39 | SMD Capacitor |  |  | CL05A104KP5NNNC
2 | 0.22uF | CAPACITOR0402_CAP | 0402_CAP | C40, C41 | SMD Capacitor |  |  | CL05A224KP5NNNC
2 | 0.47uF | CAPACITOR0402_CAP | 0402_CAP | C42, C43 | SMD Capacitor | 490-12270-1-ND |  | GRT155R61E474ME01D
8 | 1uF | CAPACITOR0201_CAP | 0201_CAP | C44, C45, C46, C47, C48, C52, C53, C74 | SMD Capacitor |  | Murata | GRM033R61A105ME44D
3 | 1uF | CAPACITOR0402_CAP | 0402_CAP | C49, C50, C51 | SMD Capacitor |  |  | GRM155R70J105KA12J
6 | 2.2uF | CAPACITOR0201_CAP | 0201_CAP | C54, C55, C56, C57, C58, C59 | SMD Capacitor |  | Murata | GRM033R61A225KE47D
3 | 4.7uF | CAPACITOR0402_CAP | 0402_CAP | C60, C67, C68 | SMD Capacitor |  |  | CL05A475MP5NRNC
6 | 4.7uF | CAPACITOR0805_CAP | 0805_CAP | C61, C62, C63, C64, C65, C66 | SMD Capacitor |  | Taiyo Yuden | JMK212ABJ475MGHT
5 | 10uF | CAPACITOR0603_CAP | 0603_CAP | C69, C70, C71, C72, C73 | SMD Capacitor | 1253-CM105X5R106M25ATCT-ND |  | CM105X5R106M25AT
1 | BICOLOR-SMD | BICOLOR-SMD | LED-0606 | D1 |  |  |  | MCL0606FRD1GR1T
1 | BICOLOR-SMD | BICOLOR-SMD | LED-0606 | D2 |  |  |  | MCL0606FYW1RD1T
1 | GREEN | LED0603 | LED-0603 | D3 | LED (Generic) | 160-1446-1-ND |  | LTST-C191KGKT
1 | DIODE0402 | DIODE0402 | 0402_DIODE | D4 |  | 641-2087-1-ND |  | CDSQR400B-HF
1 | BLM03PG330SN1D | FERRITE_BEAD0201 | 0201_FB | FB1 |  |  | Murata | BLM03PG330SN1D
DNP | FIDUCIAL1X2 | FIDUCIAL1X2 | FIDUCIAL-1X2 | FD1, FD2, FD3 | Fiducial Alignment Points
1 | USB4110-GF-A | USB4110-GF-A | GCT_USB4110-GF-A | J1 | USB-C (USB TYPE-C) USB 2.0 Receptacle Connector 24 (16+8 Dummy) Position Surface Mount, Right Angle | Through Hole |  | USB4110-GF-A
DNP | TC2030-JLINK-NL-2SIDE | TC2030-JLINK-NL-2SIDE | TC2030-IDC-NL-2SIDE | J2, J3
1 | MOLEX-PICO-SPOX-3SIDE | MOLEX-PICO-SPOX-3SIDE | MOLEX-PICO-SPOX-3_SIDE | J4 | MOLEX | WM7647CT-ND
DNP | JUMPER-SMT_2_NC_TRACE_SILK | JUMPER-SMT_2_NC_TRACE_SILK | SMT-JUMPER_2_NC_TRACE_SILK | JP1, JP7 | Normally closed trace jumper
DNP | JUMPER-SMT_3_1-NC_TRACE_SILK | JUMPER-SMT_3_1-NC_TRACE_SILK | SMT-JUMPER_3_1-NC_TRACE_SILK | JP2, JP3, JP4, JP5, JP8 | Normally closed trace jumper (1 of 2 connections)
DNP | JUMPER-SMT_2_NO_SILK | JUMPER-SMT_2_NO_SILK | SMT-JUMPER_2_NO_SILK | JP6 | Normally open jumper
DNP |  | PINHD-1X2 | 1X02 | JP9 | PIN HEADER
1 | 2.2µH | INDUCTOR0805 | 0805_CAP | L1 | A very specific inductor |  | Murata | DFE201210U-2R2M=P2
1 | 1.0µH | INDUCTOR0603 | 0603_CAP | L2 | A very specific inductor |  | Murata | DFE18SAN1R0ME0L
1 | 4.7nH | INDUCTOR0402 | 0402_CAP | L3 | A very specific inductor |  |  | LQW15AN4N7G8ZD
1 | WURTH_COIL_760308103204 | WURTH_COIL_760308103204 | WURTH_COIL_760308103204 | L4 |  | 732-5258-ND | Würth Elektronik | 7.60308E+11
2 | 10uH | INDUCTORNRX3015 | NRX3015 | L5, L6 | A very specific inductor |  | TAIYO YUDEN | NR3015T100M
1 | PUI_SMT-0440-T-2-R | PUI_SMT-0440-T-2-R | SMT-0440-T-2-R | LS1 |  | 668-SMT-0440-T-2-RTR-ND |  | SMT-0440-T-2-R
1 | CSD75207W15 | CSD75207W15 | DSBGA | Q1 | low on resistance, gate charge dual p-channel nexfet | 296-40008-1-ND | TEXAS INSTRUMENTS | CSD75207W15
1 | MOSFET-NCHANNELXFDN-3 | MOSFET-NCHANNELXFDN-3 | XFDFN-3 | Q2 | Generic NMOS footprint | DMN2400UFB4-7DICT-ND
1 | 49.9-1% | RESISTOR0201_RES | 0201_RES | R1 | Resistor |  |  | ERJ-1GNF49R9C
2 | 97.6 | RESISTOR0402_RES | 0402_RES | R2, R3 | Resistor | RMCF0402FT97R6CT-ND |  | RMCF0402FT97R6
2 | 162 | RESISTOR0402_RES | 0402_RES | R4, R5 | Resistor | RMCF0402FT162RCT-ND |  | RMCF0402FT162R
3 | 1k | RESISTOR0402_RES | 0402_RES | R6, R14, R15 | Resistor |  |  | RC0402JR-071KL
2 | 845k | RESISTOR0201_RES | 0201_RES | R7, R9 | Resistor |  |  | ERJ-1GNF8453C
1 | 422k | RESISTOR0201_RES | 0201_RES | R8 | Resistor |  |  | ERJ-1GNF4223C
1 | 261k | RESISTOR0201_RES | 0201_RES | R10 | Resistor |  |  | ERJ-1GNF2613C
2 | 15 | RESISTOR0402_RES | 0402_RES | R11, R25 | Resistor |  |  | RC0402JR-0715RL
2 | 5.1 | RESISTOR0402_RES | 0402_RES | R12, R26 | Resistor |  |  | RC0402JR-075R1L
6 | 10k | RESISTOR0402_RES | 0402_RES | R16, R20, R21, R22, R23, R24 | Resistor | 311-10KJRCT-ND |  | RC0402JR-0710KL
1 | 2.2k | RESISTOR0402_RES | 0402_RES | R17 | Resistor | RMCF0402JT2K20CT-ND |  | RMCF0402JT2K20
2 | 5.1k | RESISTOR0402_RES | 0402_RES | R18, R19 | Resistor | RMCF0402FT5K10CT-ND |  | RMCF0402FT5K10
3 | 100k | RESISTOR0402_RES | 0402_RES | R28, R29, R32 | Resistor |  |  | RT0402BRE07100KL
1 | 3.3M | RESISTOR0402_RES | 0402_RES | R30 | Resistor | RMCF0402FT3M30CT-ND |  | RMCF0402FT3M30
3 | 5.1M | RESISTOR0402_RES | 0402_RES | R31, R33, R34 | Resistor | RMCF0402FT5M10CT-ND |  | RMCF0402FT5M10
DNP | DNP | RESISTOR0603_RES | 0603-RES | R100, R101, R103 | Resistor
DNP | DNP | RESISTOR0402_RES | 0402_RES | R102 | Resistor
1 | 10k@25C | THERMISTOR0402 | 0402_RES | RT1 | Thermistor. | 490-18149-1-ND |  | NCU15XH103F60RC
1 |  | 4.50404E+11 | 4.50404E+11 | S1 | WS-SLSU Mini Slide Switch, Same Side Connection Side Push 6.7x2.7 mm | 732-13665-1-ND
1 | SKY13373 | SKY13373 | SKY13373 | S2 | 0.1 to 8.0 GHz SP3T Switch |  | Skyworks | SKY13373-460LF
1 | SIP3241XSIP32414 | SIP3241XSIP32414 | TDFN2X2X0P6-8 | S3 |  |  | Vishay | SIP32414DNP-T1-GE4
DNP | TPTP06SQ | TPTP06SQ | TP06SQ | TP_DW_CIPO, TP_DW_COPI, TP_DW_SPI_CLK, TP_DW_SPI_CS | Test pad
DNP | TEST-POINT | TEST-POINT | PAD.03X.03 | TP0, TP1, TP2, TP3, TP4, TP5, TP6, TP7, TP8, TP9, TP10, TP11, TP12, TP13, TP14, TP15, TP16, TP17, TP18, TP19, TP20
1 | APOLLO4_BLUE_SOC_BGA | APOLLO4_BLUE_SOC_BGA | APOLLO4_BLUE_SOC_BGA | U1 |  |  | ambiq | AMA4B2KK-KBR
1 | DW3210 | DW3210 | QFN40P500X500X80-40N | U2 | DW3000 QFN No PDoA |  | Qorvo | DW3210
1 | BQ24040 | BQ24040 | DSQ0010A | U3 | Simple Li Ion / Li Poly charger. | 296-37142-1-ND |  | BQ24040DSQR
1 | BQ51013B | BQ51013B | RHL0020A | U4 | bq51013B | 296-38885-1-ND |  | BQ51013BRHLR
1 | W25N01GWZEIG | W25N01GWZEIG | WSON127P800X600X80-9T430X340N | U5 |  |  | Winbond | W25N01GWZEIG
1 | BNO055 | BNO055 | LGA28R0P510X4_5P2X3P8X1 | U6 |  |  | Bosch Scientific | BNO055
1 | RT8020RT8020GQW | RT8020RT8020GQW | SON45P300X300X80-13T160X250N | VR1 |  |  | RichTek | RT8020GQW
1 | TPS7A0218PDQNR | TPS7A0218PDQNR | 4-XDFN-EP | VR2 |  |  |  | TPS7A0218PDQNR
2 | TXC-9HT12 | TXC-9HT12 | TXC-9HT12 | X1, X2 |  |  | TXC Corp | 9HT12-32.768KDZY-T
1 | ABM12W | ABM12W | ABM12W | X3 |  |  | Abracon | ABM12W-32.0000MHZ-6-D1X-T3
1 | 38.4MHz | FA-20H | FA-20H | X4 | 38.4MHz ±10ppm Crystal 8.5pF 40 Ohms 4-SMD, No Lead | SER3631CT-ND | EPSON | FA-20H 38.4000MF10Z-AS3

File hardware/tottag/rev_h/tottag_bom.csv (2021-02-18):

# Bill of Materials
# Converted from {}
# Generated by bom_to_text.py
#
Qty | Parts | Value | Can Substitute | Do Not Populate | Device | Package | Description | DESCRIPTION | DIGIKEY | MANUFACTURER | MPN | MOUSER | Notes
3 | A1, A2, A3 | TAIYO-YUDEN-AH086M | N |  | TAIYO-YUDEN-AH086M | TAIYO-YUDEN-AH086M | UWB Antenna - 3.1-8GHz |  | 587-2204-1-ND |  | AH086M555003-T
1 | A4 | AMCA72-2R47G-S1F-T | N |  | AMCA72-2R47G-S1F-T | AMCA72-2R470G-S1F-T | WiFi/Bluetooth/ZigBee, ISM Atenna | RF ANT 2.4GHZ CHIP SOLDER SMD | 535-14108-1-ND |  | AMCA72-2R470G-S1F-T4
1 | C1 | 0.5pF | ASK |  | CAPACITOR0402_CAP | 0402_CAP | SMD Capacitor |  | 490-11250-1-ND |  | GJM1555C1HR50WB01D
1 | C2 | 0.8pF | ASK |  | CAPACITOR0402_CAP | 0402_CAP | SMD Capacitor |  | 490-11253-1-ND |  | GJM1555C1HR80WB01D
1 | C3 | 1.2pF | ASK |  | CAPACITOR0402_CAP | 0402_CAP | SMD Capacitor |  | 490-3085-1-ND |  | GJM1555C1H1R2CB01D
2 | C4, C5 | 10pF | Y |  | CAPACITOR0402_CAP | 0402_CAP | SMD Capacitor |  | 732-12054-1-ND |  | 885012005074
2 | C6, C7 | 12pF | ASK |  | CAPACITOR0201_CAP | 0201_CAP | SMD Capacitor |  | 399-8604-2-ND |  | CBR02C120F3GAC
8 | C8, C9, C10, C11, C12, C13, C14, C15 | 12pF | ASK |  | CAPACITOR0402_CAP | 0402_CAP | SMD Capacitor |  | 399-8815-2-ND |  | CBR04C120F5GAC
1 | C16 | 18pF | ASK |  | CAPACITOR0402_CAP | 0402_CAP | SMD Capacitor |  | 399-8828-1-ND |  | CBR04C180F5GAC
1 | C17 | 27pF | ASK |  | CAPACITOR0402_CAP | 0402_CAP | SMD Capacitor |  | 490-16380-1-ND |  | GJM1555C1H270FB01D
1 | C18 | 47pF | Y |  | CAPACITOR0402_CAP | 0402_CAP | SMD Capacitor |  | 490-5942-1-ND |  | GRM1555C1H470JA01D
1 | C19 | 100pF | Y |  | CAPACITOR0402_CAP | 0402_CAP | SMD Capacitor |  | 490-5922-1-ND |  | GRM1555C1H101JA01D
2 | C20, C21 | 330pF | Y |  | CAPACITOR0402_CAP | 0402_CAP | SMD Capacitor |  | 311-3768-1-ND |  | CC0402JRX7R9BB331
2 | C22, C23 | 470pF | Y |  | CAPACITOR0402_CAP | 0402_CAP | SMD Capacitor | CAP CER 470PF 50V C0G/NP0 0402 | 490-6242-1-ND | Murata | GRM1555C1H471JA01J
2 | C24, C25 | 820pF | ASK |  | CAPACITOR0402_CAP | 0402_CAP | SMD Capacitor |  | 399-11129-2-ND |  | C0402C821J5GACTU
5 | C26, C27, C28, C29, C30 | 10nF | Y |  | CAPACITOR0402_CAP | 0402_CAP | SMD Capacitor |  | 490-6351-2-ND |  | GRM155R71H103KA88J
5 | C31, C32, C33, C34, C35 | 22nF | ASK |  | CAPACITOR0402_CAP | 0402_CAP | SMD Capacitor |  | 490-10699-2-ND |  | GRM155R71E223JA61D
1 | C36 | 47nF | Y |  | CAPACITOR0402_CAP | 0402_CAP | SMD Capacitor |  | 445-1264-1-ND |  | C1005X7R1C473K050BC
32 | C37, C38, C39, C40, C41, C42, C43, C44, C45, C46, C47, C48, C49, C50, C51, C52, C53, C54, C55, C56, C57, C58, C59, C60, C61, C62, C63, C64, C65, C66, C67, C68 | 0.1uF | Y |  | CAPACITOR0402_CAP | 0402_CAP | SMD Capacitor |  | 490-6328-1-ND |  | GRM155R71C104KA88J
2 | C69, C70 | 470nF | Y |  | CAPACITOR0402_CAP | 0402_CAP | SMD Capacitor |  | 490-12270-1-ND |  | GRT155R61E474ME01D
9 | C71, C72, C73, C74, C75, C76, C77, C78, C79 | 1uF | Y |  | CAPACITOR0402_CAP | 0402_CAP | SMD Capacitor |  | 490-7195-1-ND |  | GRM155R70G105KA12D
11 | C80, C81, C82, C83, C84, C85, C86, C87, C88, C89, C90 | 4.7uF | Y |  | CAPACITOR0402_CAP | 0402_CAP | SMD Capacitor | CAP CER 4.7UF 6.3V X5R 0402 | 445-5947-1-ND | TDK | C1005X5R0J475K050BC
4 | C91, C92, C93, C94 | 10uF | Y |  | CAPACITOR0603_CAP | 0603_CAP | SMD Capacitor |  | 1253-CM105X5R106M25ATCT-ND |  | CM105X5R106M25AT
1 | C95 | 47uF | Y |  | CAPACITOR0603_CAP | 0603_CAP | SMD Capacitor |  | 490-13247-1-ND |  | GRM188R60J476ME15D
1 | D1 | GREEN | Y |  | LED0603 | LED-0603 | LED (Generic) |  | 160-1446-1-ND |  | LTST-C191KGKT
2 | D2, D3 | SML-LX0404SIUPGUSB | Y |  | SML-LX0404SIUPGUSB | 1MM_SQ_4PAD | 1mm^2 RGB LED |  | 67-2125-1-ND | Lumex Opto | SML-LX0404SIUPGUSB
1 | D4 | DIODE0402 | Y |  | DIODE0402 | 0402_DIODE |  |  | 641-2087-1-ND |  | CDSQR400B-HF
1 | J1 | USB4110-GF-A | N |  | USB4110-GF-A | GCT_USB4110-GF-A | CONN USB 2.0 TYPE-C R/A SMT | USB-C (USB TYPE-C) USB 2.0 Receptacle Connector 24 (16+8 Dummy) Position Surface Mount, Right Angle | Through Hole | GCT
1 | J2 | DM3AT-SF-PEJM5 | N |  | DM3AT-SF-PEJM5 | DM3AT-SF-PEJM5 | CONN MICRO SD R/A PUSH-PUSH SMD | CONN MICRO SD CARD PUSH-PUSH R/A | HR1964CT-ND | Hirose Electric Co Ltd | DM3AT-SF-PEJM5
1 | J5 | MOLEX-PICO-SPOX-3SIDE | N |  | MOLEX-PICO-SPOX-3SIDE | MOLEX-PICO-SPOX-3_SIDE | MOLEX |  | WM7647CT-ND
1 | L1 | 4.7nH | ASK |  | INDUCTOR0402 | 0402_CAP | A very specific inductor |  | 490-15482-1-ND |  | LQW15AN4N7G8ZD
1 | L2 | 15nH | ASK |  | INDUCTOR0402 | 0402_CAP | A very specific inductor |  | 587-1521-1-ND |  | HK100515NJ-T
1 | L3 | 10uH | ASK |  | INDUCTOR0603 | 0603_CAP | A very specific inductor |  | 490-4025-1-ND |  | LQM18FN100M00D
1 | L4 | WURTH_COIL_760308103204 | N |  | WURTH_COIL_760308103204 | WURTH_COIL_760308103204 |  |  | 732-5258-ND | Würth Elektronik | 760308103204 |  | Coil should be on top of board, centered, with coil side facing up
1 | LS1 | PUI_SMT-0440-T-2-R | N |  | PUI_SMT-0440-T-2-R | SMT-0440-T-2-R |  |  | 668-SMT-0440-T-2-RTR-ND |  | SMT-0440-T-2-R
2 | Q1, Q2 | CSD75207W15 | ASK |  | CSD75207W15 | DSBGA | low on resistance, gate charge dual p-channel nexfet |  | 296-40008-1-ND | TEXAS INSTRUMENTS | CSD75207W15
1 | R1 | 4.7 | Y |  | RESISTOR0402_RES | 0402_RES | Resistor |  | RMCF0402FT4R70CT-ND |  | RMCF0402FT4R70
2 | R2, R3 | 97.6 | ASK |  | RESISTOR0402_RES | 0402_RES | Resistor |  | RMCF0402FT97R6CT-ND |  | RMCF0402FT97R6
2 | R4, R5 | 162 | ASK |  | RESISTOR0402_RES | 0402_RES | Resistor |  | RMCF0402FT162RCT-ND |  | RMCF0402FT162R
1 | R6 | 270 | Y |  | RESISTOR0402_RES | 0402_RES | Resistor |  | RMCF0402FT270RCT-ND |  | RMCF0402FT270R
9 | R7, R8, R9, R10, R11, R12, R13, R14, R15 | 1k | Y |  | RESISTOR0402_RES | 0402_RES | Resistor |  | RMCF0402FT1K00CT-ND |  | RMCF0402FT1K00
1 | R16 | 1.41k | Y |  | RESISTOR0402_RES | 0402_RES | Resistor |  | RMCF0402FT1K40CT-ND |  | RMCF0402FT1K40
1 | R17 | 2.2k | Y |  | RESISTOR0402_RES | 0402_RES | Resistor |  | RMCF0402JT2K20CT-ND |  | RMCF0402JT2K20
2 | R18, R19 | 5.1k | Y |  | RESISTOR0402_RES | 0402_RES | Resistor |  | RMCF0402FT5K10CT-ND |  | RMCF0402FT5K10
7 | R20, R21, R22, R23, R24, R25, R26 | 10k | Y |  | RESISTOR0402_RES | 0402_RES | Resistor |  | 311-10KJRCT-ND |  | RC0402JR-0710KL
2 | R27, R28 | 11k | Y |  | RESISTOR0402_RES | 0402_RES | Resistor |  | RMCF0402FT11K0CT-ND |  | RMCF0402FT11K0
1 | R29 | 16k | Y |  | RESISTOR0402_RES | 0402_RES | Resistor |  | RMCF0402FT16K0CT-ND |  | RMCF0402FT16K0
7 | R30, R31, R32, R33, R34, R35, R36 | 100k | Y |  | RESISTOR0402_RES | 0402_RES | Resistor
1 | R37 | 3.3M | Y |  | RESISTOR0402_RES | 0402_RES | Resistor |  | RMCF0402FT3M30CT-ND |  | RMCF0402FT3M30
1 | R38 | 10M | Y |  | RESISTOR0402_RES | 0402_RES | Resistor |  | RMCF0402FT10M0CT-ND |  | RMCF0402FT10M0
1 | R39 | DNP |  | DNP | RESISTOR0402_RES | 0402_RES | Resistor
1 | RT1 | 10k@25C | ASK |  | THERMISTOR0402 | 0402_RES | Thermistor. |  | 490-18149-1-ND |  | NCU15XH103F60RC
1 | S1 |  | N |  | 450404015514 | 450404015514 | WS-SLSU Mini Slide Switch, Same Side Connection Side Push 6.7x2.7 mm |  | 732-13665-1-ND
1 | T1 | HHM1595A1 | N |  | HHM1595A1 | EIA-0805 | Description: Symbol for HHM1595A1, a multilayer Balun from TDK. | XFMR BALUN RF 3.0-8.0GHZ UWB SMD | 445-3387-1-ND | TDK Corporation | HHM1595A1 | 810-HHM1595A1
1 | U1 | DW1000 | N |  | DW1000 | QFN-48-DW1000 | Description: The DecaWave DW1000 chip, used for UWB two-way ranging. | IC RF TXRX 802.15.4 48-QFN | 1479-1001-1-ND | Decawave Limited | DW1000-I-TR13
1 | U2 | BQ24040 | N |  | BQ24040 | DSQ0010A | Simple Li Ion / Li Poly charger. |  | 296-37142-1-ND |  | BQ24040DSQR
1 | U3 | LSM6DSOXTR | N |  | LSM6DSOXTR | LGA-14L_STM |  |  | 497-18367-1-ND |  | LSM6DSOXTR
1 | U4 | 1.8V | N |  | XCL206B | XCL20X | Non-Isolated PoL Module DC DC Converter 1 Output 1.8V 600mA 2V - 6V Input |  | 893-1406-2-ND |  | XCL206B183CR-G
1 | U5 | MAX8887EZK33+T | N |  | MAX8887EZK33+T | SOT-23-5 | IC REG LDO 3.3V 0.3A TSOT23-5 |  | MAX8887EZK33+TCT-ND
1 | U6 | BQ51013B | N |  | BQ51013B | RHL0020A | bq51013B |  | 296-38885-1-ND |  | BQ51013BRHLR
1 | U7 | NRF52840 | N |  | NRF52840 | AQFN73 | ultra-low power 2.4 GHz wireless system on chip (SoC) integrating a multiprotocol 2.4 GHz transceiver, an ARM® Cortex®-M4F CPU. |  | 1490-1071-1-ND | NORIDIC SEMICONDUCTOR | NRF52840-QIAA-R
1 | U8 | SIP32510 | N |  | SIP32510 | TSOT23-6 | Load switch, slew rate controlled. By Vishay |  | SIP32510DT-T1-GE3CT-ND | Vishay | SIP32510DT-T1-GE3
1 | U9 | SKY13317 | N |  | SKY13317 | MLPQ-UT-8 | Description: Device for SKY13317-373LF, an RF switch from Skyworks Inc. | IC SWITCH RF SP3T 8-MLP | 863-1056-1-ND | Skyworks Solutions Inc. | SKY13317-373LF
1 | U10 | STM32F091CC | N |  | STM32F091CC | UFQFPN-48 | Description: STM32F091CC from STMicroelectronics, an ARM-based 32-bit MCU with 256 kB Flash, 32kB of SRAM and a Cortex M0 | IC MCU 32BIT 256KB FLASH 48QFPN | 497-15813-ND | STMicroelectronics | STM32F091CCU6 | 511-STM32F091CCU6
1 | U11 | AB1815-T3 | N |  | AB1815-T3 | QFN-16-3MM | Ultra-low current RTC. 55nA quiescent @ 3V. 1.5-3.6V input. |  | 535-11936-1-ND | Abracon | AB1815-T3
1 | U12 | LIS3MDL | N |  | LIS3MDL | LGA-12 |  |  | 497-13892-1-ND | STM | LIS3MDLTR
1 | X1 | 32.768kHz | N |  | ABS05-32.768KHZ-9-T | ABS05 | 32.768kHz Crystal |  | 535-11897-1-ND | Abracon | ABS05-32.768KHZ-9-T
1 | X2 | 16MHz | N |  | FA-20H | FA-20H | Description: Oscillator by EPSON from 12MHz to 54 MHz | 16MHz ±10ppm Crystal 8pF 80 Ohms 4-SMD, No Lead | SER3913CT-ND | EPSON | FA-20H 16.0000MF10Z-AJ3
1 | X3 | 32MHz | N |  | 7V-32.000MAHV-T | TXC-7V | TXC CRYSTAL SMD |  | 887-2568-1-ND | TXC CORPORATION | 7M-32.000MAHV-T
1 | X4 | 38.4MHz | N |  | FA-20H | FA-20H | Description: Oscillator by EPSON from 12MHz to 54 MHz | 38.4MHz ±10ppm Crystal 8.5pF 40 Ohms 4-SMD, No Lead | SER3631CT-ND | EPSON | FA-20H 38.4000MF10Z-AS3
1 | X5 | ABS07-32.768KHZ-7-T | N |  | ABS07-32.768KHZ-7-T | ABS07 | 32.768kHz Crystal |  | 535-9543-1-ND | ABRACON | ABS07-32.768KHZ-7-T
1 | B1 |  |  | DNP | MS518SE | MS518SE-FL35E | A small, low leakage rechargeable battery for RTC backup |  | 728-1054-ND | Seiko | MS518SE-FL35E
1 | JP1 | JUMPER-SMT_2_NO_SILK |  | DNP | JUMPER-SMT_2_NO_SILK | SMT-JUMPER_2_NO_SILK | Normally open jumper
2 | JP2, JP3 | JUMPER-SMT_3_1-NC_TRACE_SILK |  | DNP | JUMPER-SMT_3_1-NC_TRACE_SILK | SMT-JUMPER_3_1-NC_TRACE_SILK | Normally closed trace jumper (1 of 2 connections)
1 | JP4 | JUMPER-SMT_2_NC_TRACE_SILK |  | DNP | JUMPER-SMT_2_NC_TRACE_SILK | SMT-JUMPER_2_NC_TRACE_SILK | Normally closed trace jumper
2 | J3, J4 | TC2030-JLINK-NL-2SIDE |  | DNP | TC2030-JLINK-NL-2SIDE | TC2030-IDC-NL-2SIDE
3 | J6, J7, J8 |  |  | DNP | PINHD-1X1 | 1X01 | PIN HEADER
22 | GP0, GP1, TP5, TP6, TP10, TP11, TP12, TP13, TP16, TP17, TP18, TP19, TP20, TP21, TP22, TP23, TP24, TP25, TP26, TP27, TP28, TP29 | TEST-POINT |  | DNP | TEST-POINT | PAD.03X.03
10 | +1V8, DW_SPI_CS, MISO, MOSI, SPI_CLK, TP1, TP2, TP3, TP4, TP15 | TPTP06SQ |  | DNP | TPTP06SQ | TP06SQ | Test pad

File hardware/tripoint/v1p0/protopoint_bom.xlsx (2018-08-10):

Reference | Quantity | Value | Footprint | ManPartNo | Digikey | DigiReel | Alternate
C34 | 1 | 1.2pF | Capacitors_SMD:C_0201 | GRM0335C1H1R2CA01D | 490-6119-1-ND | 490-6119-6-ND
C1, C3, C11 | 3 | 10pF | Capacitors_SMD:C_0201 | GRM0335C1E100JA01D | 490-8607-1-ND | 490-8607-6-ND
C25, C26, C32, C36 | 4 | 12pF | Capacitors_SMD:C_0201 | GRM0335C1E120JA01D | 490-3144-1-ND | 490-3144-6-ND
C37, C38 | 2 | 12pF | Capacitors_SMD:C_0402 | GRM0335C1E120JA01D | 490-5924-1-ND | 490-5924-6-ND
C35 | 1 | 18pF | Capacitors_SMD:C_0201 | GRM0335C1H180JA01D | 490-6117-1-ND | 490-6117-6-ND
C30 | 1 | 27pF | Capacitors_SMD:C_0201 | GRM0335C1E270JA01D | 490-3150-1-ND | 490-3150-6-ND
C8, C10, C17 | 3 | 100pF | Capacitors_SMD:C_0201 | GRM0335C1E101JA01D | 490-3160-1-ND | 490-3160-6-ND
C5, C7 | 2 | 330pF | Capacitors_SMD:C_0201 | GRM033R71E331KA01D | 490-3178-1-ND | 490-3178-6-ND
C31 | 1 | 820pF | Capacitors_SMD:C_0201 | GRM033R71E821KA01D | 490-3183-1-ND | 490-3183-6-ND
C12 | 1 | 0.01uF | Capacitors_SMD:C_0201 | GRM033R71A103KA01D | 490-3194-1-ND | 490-3194-6-ND
C2, C6, C9, C13, C14, C15, C16, C18, C19, C20, C21, C23, C24, C27, C28, C29 | 16 | 0.1uF | Capacitors_SMD:C_0201 | GRM033R61A104KE15D | 490-5881-1-ND | 490-5881-6-ND
C4, C22 | 2 | 4.7uF | Capacitors_SMD:C_0603 | GRM188F51A475ZE20D | 490-3302-1-ND | 490-3302-6-ND
C33 | 1 | 10uF | Capacitors_SMD:C_0603 | GRM188R61C106MA73D | 490-7201-1-ND | 490-7201-6-ND
R4 | 1 | 270 | Resistors_SMD:R_0201 | ERJ-1GEF2700C | P270ABCT-ND | P270ABDKR-ND
R1 | DNP | 11k | Resistors_SMD:R_0201 | ERJ-1GEF1102C | P11.0KABCT-ND | P11.0KABDKR-ND
R2, R5 | 2 | 11k | Resistors_SMD:R_0201 | ERJ-1GEF1102C | P11.0KABCT-ND | P11.0KABDKR-ND
R3 | 1 | 16k | Resistors_SMD:R_0201 | ERJ-1GEF1602C | P16.0KABCT-ND | P16.0KABDKR-ND
T1 | 1 | HHM1595A1 | polypoint:HHM1595A1 | HHM1595A1 | 445-3387-1-ND | 445-3387-6-ND
U1 | 1 | STM32F031G6U6 | polypoint:UFQFPN-28 | STM32F031G6U6 | 497-13620-ND
U2 | 1 | LXDC2HL | polypoint:LXDC2HL | LXDC2HL18A-052 | 490-5791-1-ND | 490-5791-6-ND
U3 | 1 | DW1000 | polypoint:QFN-48-EP-6x6mm | DW1000-I-TR13 | 1479-1001-1-ND | 1479-1001-6-ND
U4 | 1 | SKY13317 | polypoint:MLPQ-UT-8-1.5X1.5mm | SKY13317-373LF | 863-1056-1-ND | 863-1056-6-ND
X1 | 1 | CRYSTAL_SMD_4 | polypoint:FA-128 | FA-20H 16.0000MF10Z-AJ3 | SER3913CT-ND | SER3913DKR-ND | 644-1059-6-ND
X2 | 1 | CRYSTAL_SMD_4 | polypoint:FA-128 | FA-20H 38.4000MF10Z-AS3 | SER3631CT-ND | SER3631DKR-ND

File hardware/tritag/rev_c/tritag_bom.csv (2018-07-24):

# Bill of Materials
# Converted from {}
# Generated by bom_to_text.py
#
Qty | Value | Device | Package | Parts | Description | DATASHEET | DESCRIPTION | DIGIKEY | MANUFACTURER | MF | MOUSER | MPN | NEWARK | OC_FARNELL | OC_NEWARK | TP_SIGNAL_NAME
3 | TAIYO-YUDEN-AH086M | TAIYO-YUDEN-AH086M | TAIYO-YUDEN-AH086M | A1,A2,A3 | UWB Antenna - 3.1-8GHz |  |  | 587-2204-1-ND
1 | ANT3216A063R2400A | ANT3216A063R2400A | ANT3216A063R2400A | A4 | Yageo 2.4GHz |  |  | 311-1542-1-ND | YAGEO |  |  | ANT3216A063R2400A
2 | 1pF | CAPACITOR0402_CAP | 0402_CAP | C1,C2 | SMD Capacitor |  |  | 712-1266-1-ND
1 | 1.2pF | CAPACITOR0402_CAP | 0402_CAP | C3 | SMD Capacitor |  |  | 490-3085-1-ND
2 | 10pF | CAPACITOR0402_CAP | 0402_CAP | C4,C5 | SMD Capacitor |  |  | 732-12054-1-ND
2 | 12pF | CAPACITOR0201_CAP | 0201_CAP | C6,C7 | SMD Capacitor |  |  | 712-1208-1-ND
8 | 12pF | CAPACITOR0402_CAP | 0402_CAP | C8,C9,C10,C11,C12,C13,C14,C15 | SMD Capacitor |  |  | 490-11190-1-ND |  |  |  | GJM1555C1H120FB01D
1 | 18pF | CAPACITOR0402_CAP | 0402_CAP | C16 | SMD Capacitor |  |  | 490-14582-1-ND
1 | 27pF | CAPACITOR0402_CAP | 0402_CAP | C17 | SMD Capacitor |  |  | 1276-1153-1-ND
1 | 100pF | CAPACITOR0402_CAP | 0402_CAP | C18 | SMD Capacitor |  |  | 399-17545-1-ND |  |  |  | C0402C101J5RACAUTO
2 | 330pF | CAPACITOR0402_CAP | 0402_CAP | C19,C20 | SMD Capacitor |  |  | 311-3768-1-ND
2 | 820pF | CAPACITOR0402_CAP | 0402_CAP | C21,C22 | SMD Capacitor |  |  | 1276-6989-1-ND |  |  |  | CL05C821JB5NFNC
3 | 10nF | CAPACITOR0402_CAP | 0402_CAP | C23,C24,C25 | SMD Capacitor |  |  | 399-1279-1-ND
1 | 47nF | CAPACITOR0402_CAP | 0402_CAP | C26 | SMD Capacitor |  |  | 445-1264-1-ND |  |  |  | C1005X7R1C473K050BC
27 | 0.1uF | CAPACITOR0402_CAP | 0402_CAP | C27,C28,C29,C30,C31,C32,C33,C34,C35,C36,C37,C38,C39,C40,C41,C42,C43,C44,C45,C46,C47,C48,C49,C50,C51,C52,C53 | SMD Capacitor |  |  | 1276-1234-1-ND
4 | 1uF | CAPACITOR0402_CAP | 0402_CAP | C54,C55,C56,C57 | SMD Capacitor |  |  | 1276-6805-1-ND
11 | 4.7uF | CAPACITOR0402_CAP | 0402_CAP | C58,C59,C60,C61,C62,C63,C64,C65,C66,C67,C68 | SMD Capacitor |  |  | 490-14306-1-ND
2 | 10uF | CAPACITOR0603_CAP | 0603_CAP | C69,C70 | SMD Capacitor |  |  | 490-10474-1-ND |  |  |  | GRM188R61A106KE69D
1 | GREEN | LED0603 | LED-0603 | D1 | LED (Generic) |  |  | 160-1446-1-ND |  |  |  | LTST-C191KGKT
2 | SML-LX0404SIUPGUSB | SML-LX0404SIUPGUSB | 1MM_SQ_4PAD | D2,D3 | 1mm^2 RGB LED |  |  | 67-2125-1-ND |  |  |  | SML-LX0404SIUPGUSB
1 | CON_MICRO_SDDM3AT-SF-PEJM5 | CON_MICRO_SDDM3AT-SF-PEJM5 | DM3AT-SF-PEJM5 | J2 | CONN MICRO SD R/A PUSH-PUSH SMD |  |  | HR1964CT-ND
1 | MICRO_USB_B_HIROSE_ZX62-B-5PA(11) | MICRO_USB_B_HIROSE_ZX62-B-5PA(11) | USB_MICRO_B-HIROSE-ZX62-B-5PA(11) | J3 | Connector Receptacle USB - micro B 2.0 5 Position Surface Mount, Right Angle, Horizontal |  |  | H125270CT-ND |  |  |  | ZX62-B-5PA(33)
1 | 3.9nH | INDUCTOR0402 | 0402_CAP | L1 | A very specific inductor |  |  | AISC-0402-3N9G-TCT-ND |  |  |  | AISC-0402-3N9G-T
1 | 15nH | INDUCTOR0402 | 0402_CAP | L2 | A very specific inductor |  |  | 587-1521-1-ND |  |  |  | HK100515NJ-T
1 | 10uH | INDUCTOR0603 | 0603_CAP | L6 | A very specific inductor |  |  | 445-6755-1-ND |  |  |  | MLZ1608N100LT000
2 | 0 | RESISTOR0402_RES | 0402_RES | R1,R2 | Resistor |  |  | P0.0JCT-ND |  |  |  | ERJ-2GE0R00X
1 | 270 | RESISTOR0402_RES | 0402_RES | R3 | Resistor |  |  | 1276-3970-1-ND |  |  |  | RC1005F271CS
3 | 470 | RESISTOR0402_RES | 0402_RES | R4,R5,R6 | Resistor |  |  | 541-4072-1-ND
4 | 1k | RESISTOR0402_RES | 0402_RES | R7,R8,R9,R10 | Resistor |  |  | 541-3240-1-ND
1 | 2k 1% | RESISTOR0402_RES | 0402_RES | R11 | Resistor |  |  | P2.00KLCT-ND
3 | 10k | RESISTOR0402_RES | 0402_RES | R12,R13,R14 | Resistor |  |  | P10KJCT-ND
2 | 11k 1% | RESISTOR0402_RES | 0402_RES | R15,R16 | Resistor |  |  | P11.0KLCT-ND
1 | 16k | RESISTOR0402_RES | 0402_RES | R17 | Resistor |  |  | YAG5263CT-ND
3 | 100k | RESISTOR0402_RES | 0402_RES | R18,R19,R20 | Resistor |  |  | 541-3960-1-ND
1 | 2.2M | RESISTOR0402_RES | 0402_RES | R21 | Resistor |  |  | 541-4083-1-ND
1 | 10M | RESISTOR0402_RES | 0402_RES | R22 | Resistor |  |  | P10MJCT-ND
1 | HHM1595A1 | HHM1595A1 | EIA-0805 | T1 | Description: Symbol for HHM1595A1, a multilayer Balun from TDK. | https://product.tdk.com/info/en/documents/data_sheet/rf_balun_hhm1595a1_en.pdf | XFMR BALUN RF 3.0-8.0GHZ UWB SMD | 445-3387-1-ND | TDK Corporation |  | 810-HHM1595A1 | HHM1595A1
1 | DW1000 | DW1000 | QFN-48-DW1000 | U1 | Description: The DecaWave DW1000 chip, used for UWB two-way ranging. | https://www.decawave.com/sites/default/files/resources/dw1000-datasheet-v2.13.pdf | IC RF TXRX 802.15.4 48-QFN | 1479-1001-1-ND | Decawave Limited |  |  | DW1000-I-TR13
1 | FT232RQ | FT232RQ | QFN32 | U2 | Source: http://www.ftdichip.com/Documents/DataSheets/DS_FT232R_v104.pdf |  |  | 768-1008-1-ND |  |  |  | FT232RQ |  | 1146033 | 91K9919
1 | LIS2DW12 | LIS2DW12 | LGA-12 | U3 | ultra low power 3 axis accelerometer |  |  | 497-17718-1-ND | STMicroelectronics |  | 511-LIS2DW12TR | LIS2DW12TR
1 | LXDC2HN18A | LXDC2HN18A | LXDC2HN | U4 | Description: Symbol for LXDC2HN18A-097, a DC-DC converter by Murata Electronics. | https://www.murata.com/~/media/webrenewal/campaign/ads/america/udcdc/lxdc_product_brief.ashx | DC/DC CONVERTER SMD | 490-12092-1-ND | Murata Electronics North America |  |  | LXDC2HN18A-097
1 | MAX8887EZK33+T | MAX8887EZK33+T | SOT-23-5 | U5 | IC REG LDO 3.3V 0.3A TSOT23-5 |  |  | MAX8887EZK33+TCT-ND
1 | MCP73831 | MCP73831 | DFN-8-MCP | U6 | Description: Device for MCP73831, a battery charge controller from Microchip. | http://ww1.microchip.com/downloads/en/DeviceDoc/20001984g.pdf | IC CONTROLLER LI-ION 4.2V 8DFN | MCP73831T-2ACI/MCCT-ND | Microchip Technology |  | 579-MCP73832T-2ACIMC | MCP73831T-2ACI/MC
1 | NRF52840 | NRF52840 | AQFN73 | U7 | ultra-low power 2.4 GHz wireless system on chip (SoC) integrating a multiprotocol 2.4 GHz transceiver, an ARM® Cortex®-M4F CPU. |  |  | 1490-1071-1-ND | NORIDIC SEMICONDUCTOR |  |  | NRF52840
1 | SIP32510 | SIP32510 | TSOT23-6 | U8 | Load switch, slew rate controlled. By Vishay |  |  | SIP32510DT-T1-GE3CT-ND | Vishay |  |  | SIP32510DT-T1-GE3
1 | SKY13317 | SKY13317 | MLPQ-UT-8 | U9 | Description: Device for SKY13317-373LF, an RF switch from Skyworks Inc. | http://www.skyworksinc.com/uploads/documents/SKY13317_373LF_200914K.pdf | IC SWITCH RF SP3T 8-MLP | 863-1056-1-ND | Skyworks Solutions Inc. |  |  | SKY13317-373LF
1 | STM32F091CC | STM32F091CC | UFQFPN-48 | U10 | Description: STM32F091CC from STMicroelectronics, an ARM-based 32-bit MCU with 256 kB Flash, 32kB of SRAM and a Cortex M0 | https://www.st.com/resource/en/datasheet/stm32f091cc.pdf | IC MCU 32BIT 256KB FLASH 48QFPN | 497-15813-ND | STMicroelectronics |  | 511-STM32F091CCU6 | STM32F091CCU6
1 | 32.768kHz | ABS05-32.768KHZ-9-T | ABS05 | X1 | 32.768kHz Crystal |  |  | 535-11897-1-ND | Abracon |  |  | FA-20H 16.0000MF10Z-AJ5
1 | 16MHz | FA-20H | FA-20H | X2 | Description: Oscillator by EPSON from 12MHz to 54 MHz | https://support.epson.biz/td/api/doc_check.php?dl=brief_FA-20H_en.pdf | 16MHz ±10ppm Crystal 8pF 80 Ohms 4-SMD, No Lead | SER4201CT-ND | EPSON
1 | 32MHz | 7V-32.000MAHV-T | TXC-7V | X3 | TXC CRYSTAL SMD |  |  | 887-1913-1-ND | TXC CORPORATION |  |  | 7M-32.000MAAE-T
1 | 38.4MHz | FA-20H | FA-20H | X4 | Description: Oscillator by EPSON from 12MHz to 54 MHz | https://support.epson.biz/td/api/doc_check.php?dl=brief_FA-20H_en.pdf | 38.4MHz ±10ppm Crystal 8.5pF 40 Ohms 4-SMD, No Lead | SER3631CT-ND | EPSON

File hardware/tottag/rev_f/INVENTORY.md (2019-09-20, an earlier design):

Where Are TotTags?
==================

Isn't this a meta question.

First Manufacturing Run (16 devices `C0:98:E5:42:00:20-2F`)
-----------------------------------------------------------

| Tag IDs  | Location
|----------|------------------------
| `20-25`  | Pat / Berkeley
| `26-2D`  | Vanderbilt
| `2E-2F`  | Zürich

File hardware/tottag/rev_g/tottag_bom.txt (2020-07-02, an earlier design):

# Bill of Materials
# Converted from tottag_bom.xlsx
# Generated by bom_to_text.py
#
# # Bill of Materials                                                                                                                                                                                                                                                                                                                                                                                                                                                                                                                                                                                                               
# # Converted from {}                                                                                                                                                                                                                                                                                                                                                                                                                                                                                                                                                                                                               
# # Generated by bom_to_text.py                                                                                                                                                                                                                                                                                                                                                                                                                                                                                                                                                                                                     
# #                                                                                                                                                                                                                                                                                                                                                                                                                                                                                                                                                                                                                                 
#                                                                                                                                                                                                                                                                                                                                                                                                                                                                                                                                                                                                                                   
# Qty                            Parts                                                                                                                                            Value                         Can Substitue  Do Not Populate (DNP)  Device                        Package                       Description                                                                                                                      DESCRIPTION                                                                                          DIGIKEY                      MANUFACTURER             MPN                   MOUSER
3                                A1, A2, A3                                                                                                                                       TAIYO-YUDEN-AH086M            N                                     TAIYO-YUDEN-AH086M            TAIYO-YUDEN-AH086M            UWB Antenna - 3.1-8GHz                                                                                                                                                                                                                587-2204-1-ND                                         AH086M555003-T        
1                                A4                                                                                                                                               AMCA72-2R47G-S1F-T            N                                     AMCA72-2R47G-S1F-T            AMCA72-2R470G-S1F-T           WiFi/Bluetooth/ZigBee, ISM Atenna                                                                                                RF ANT 2.4GHZ CHIP SOLDER SMD                                                                        535-14108-1-ND                                        AMCA72-2R470G-S1F-T4  
1                                C1                                                                                                                                               0.5pF                         ASK                                   CAPACITOR0402_CAP             0402_CAP                      SMD Capacitor                                                                                                                                                                                                                         490-11250-1-ND                                        GJM1555C1HR50WB01D    
1                                C2                                                                                                                                               0.8pF                         ASK                                   CAPACITOR0402_CAP             0402_CAP                      SMD Capacitor                                                                                                                                                                                                                         490-11253-1-ND                                        GJM1555C1HR80WB01D    
1                                C3                                                                                                                                               1.2pF                         ASK                                   CAPACITOR0402_CAP             0402_CAP                      SMD Capacitor                                                                                                                                                                                                                         490-3085-1-ND                                         GJM1555C1H1R2CB01D    
2                                C4, C5                                                                                                                                           10pF                          Y                                     CAPACITOR0402_CAP             0402_CAP                      SMD Capacitor                                                                                                                                                                                                                         732-12054-1-ND                                        885012005074          
2                                C6, C7                                                                                                                                           12pF                          ASK                                   CAPACITOR0201_CAP             0201_CAP                      SMD Capacitor                                                                                                                                                                                                                         399-8604-2-ND                                         CBR02C120F3GAC        
8                                C8, C9, C10, C11, C12, C13, C14, C15                                                                                                             12pF                          ASK                                   CAPACITOR0402_CAP             0402_CAP                      SMD Capacitor                                                                                                                                                                                                                         399-8815-2-ND                                         CBR04C120F5GAC        
1                                C16                                                                                                                                              18pF                          ASK                                   CAPACITOR0402_CAP             0402_CAP                      SMD Capacitor                                                                                                                                                                                                                         399-8828-1-ND                                         CBR04C180F5GAC        
1                                C17                                                                                                                                              27pF                          ASK                                   CAPACITOR0402_CAP             0402_CAP                      SMD Capacitor                                                                                                                                                                                                                         490-16380-1-ND                                        GJM1555C1H270FB01D    
1                                C18                                                                                                                                              47pF                          Y                                     CAPACITOR0402_CAP             0402_CAP                      SMD Capacitor                                                                                                                                                                                                                         490-5942-1-ND                                         GRM1555C1H470JA01D    
1                                C19                                                                                                                                              100pF                         Y                                     CAPACITOR0402_CAP             0402_CAP                      SMD Capacitor                                                                                                                                                                                                                         490-5922-1-ND                                         GRM1555C1H101JA01D    
2                                C20, C21                                                                                                                                         330pF                         Y                                     CAPACITOR0402_CAP             0402_CAP                      SMD Capacitor                                                                                                                                                                                                                         311-3768-1-ND                                         CC0402JRX7R9BB331     
2                                C22, C23                                                                                                                                         470pF                         Y                                     CAPACITOR0402_CAP             0402_CAP                      SMD Capacitor                                                                                                                    CAP CER 470PF 50V C0G/NP0 0402                                                                       490-6242-1-ND                Murata                   GRM1555C1H471JA01J    
2                                C24, C25                                                                                                                                         820pF                         ASK                                   CAPACITOR0402_CAP             0402_CAP                      SMD Capacitor                                                                                                                                                                                                                         399-11129-2-ND                                        C0402C821J5GACTU      
5                                C26, C27, C28, C29, C30                                                                                                                          10nF                          Y                                     CAPACITOR0402_CAP             0402_CAP                      SMD Capacitor                                                                                                                                                                                                                         490-6351-2-ND                                         GRM155R71H103KA88J    
5                                C31, C32, C33, C34, C35                                                                                                                          22nF                          ASK                                   CAPACITOR0402_CAP             0402_CAP                      SMD Capacitor                                                                                                                                                                                                                         311-3823-1-ND                                         CC0402ZRY5V8BB223     
1                                C36                                                                                                                                              47nF                          Y                                     CAPACITOR0402_CAP             0402_CAP                      SMD Capacitor                                                                                                                                                                                                                         445-1264-1-ND                                         C1005X7R1C473K050BC   
29                               C37, C38, C39, C40, C41, C42, C43, C44, C45, C46, C47, C48, C49, C50, C51, C52, C53, C54, C55, C56, C57, C58, C59, C60, C61, C62, C63, C64, C65  0.1uF                         Y                                     CAPACITOR0402_CAP             0402_CAP                      SMD Capacitor                                                                                                                                                                                                                         399-C0402C104K4RAC7411TR-ND                           C0402C104K4RAC7411    
2                                C66, C67                                                                                                                                         470nF                         Y                                     CAPACITOR0402_CAP             0402_CAP                      SMD Capacitor                                                                                                                                                                                                                         490-12270-1-ND                                        GRT155R61E474ME01D    
8                                C68, C69, C70, C71, C72, C73, C74, C75                                                                                                           1uF                           Y                                     CAPACITOR0402_CAP             0402_CAP                      SMD Capacitor                                                                                                                                                                                                                         490-7195-1-ND                                         GRM155R70G105KA12D    
11                               C76, C77, C78, C79, C80, C81, C82, C83, C84, C85, C86                                                                                            4.7uF                         Y                                     CAPACITOR0402_CAP             0402_CAP                      SMD Capacitor                                                                                                                    CAP CER 4.7UF 6.3V X5R 0402                                                                          445-13820-2-ND               TDK                      C1005X5R1A475K050BC   
5                                C87, C88, C89, C90, C91                                                                                                                          10uF                          Y                                     CAPACITOR0603_CAP             0603_CAP                      SMD Capacitor                                                                                                                                                                                                                         1253-CM105X5R106M25ATCT-ND                            CM105X5R106M25AT      
1                                C92                                                                                                                                              47uF                          Y                                     CAPACITOR0603_CAP             0603_CAP                      SMD Capacitor                                                                                                                                                                                                                         490-13247-1-ND                                        GRM188R60J476ME15D
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

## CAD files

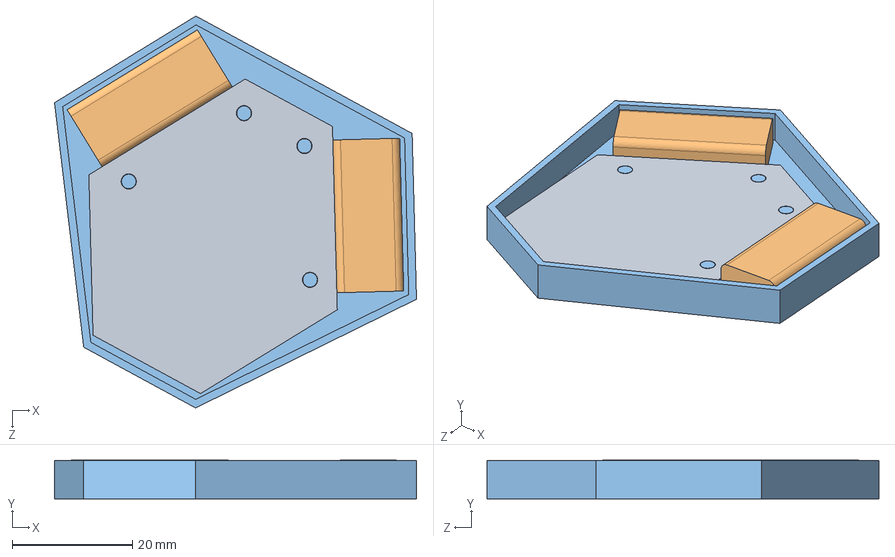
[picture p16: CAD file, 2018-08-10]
hardware/cad/tritag-board/device.SLDASM
60.2 x 6.41 x 65.1 mm
pcb
battery_110mAh x 2
case_bottom

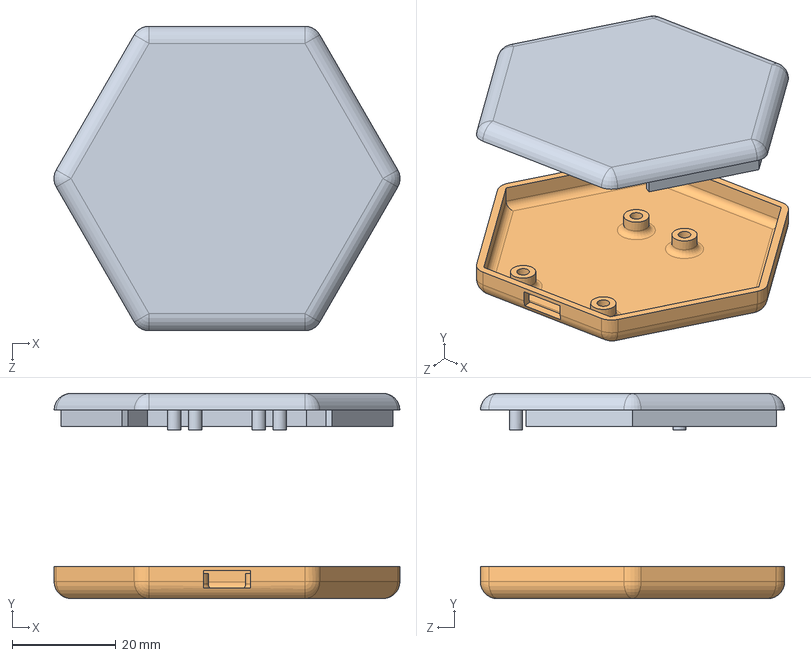
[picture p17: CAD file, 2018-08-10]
hardware/cad/tritag-case/tritag_case.SLDASM
66.6 x 39.5 x 58.6 mm
tritag_case_top
tritag_case_bottom

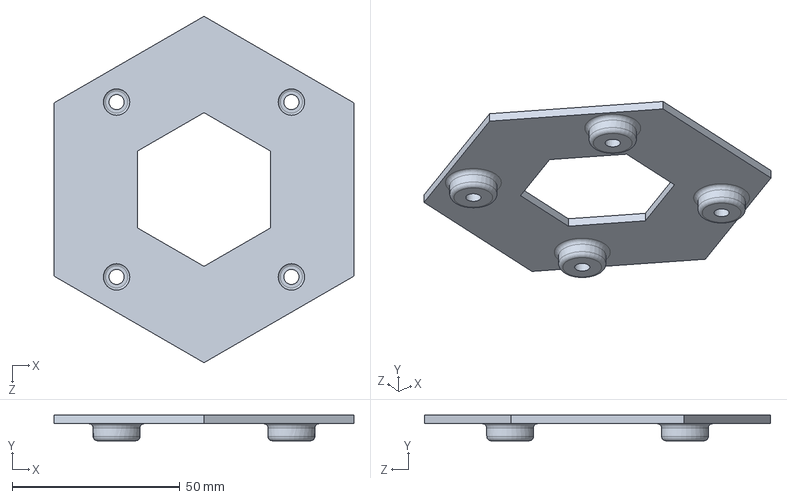
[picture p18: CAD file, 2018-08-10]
hardware/cad/polypoint-mount/backplate_hexagon.SLDPRT
89.3 x 7.62 x 103.2 mm

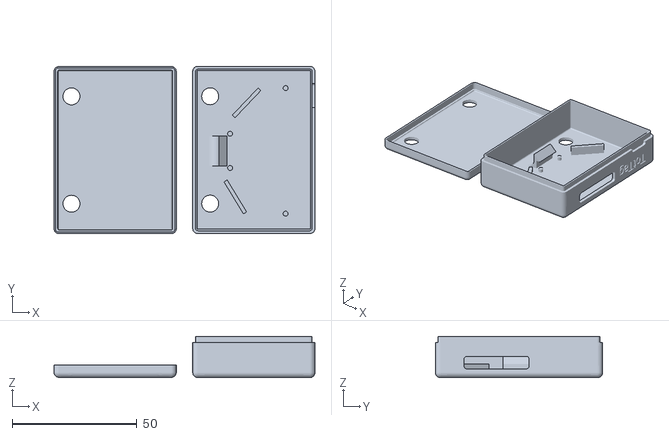
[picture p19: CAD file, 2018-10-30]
hardware/cad/tottag-case/case_v7.stl
104.6 x 67.0 x 16.5

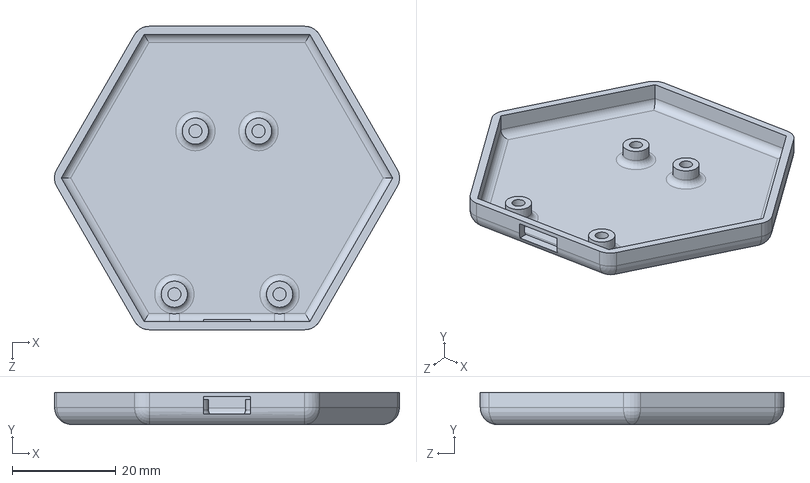
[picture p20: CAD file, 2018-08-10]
hardware/cad/tritag-case/tritag_case_bottom.SLDPRT
66.6 x 6.22 x 58.6 mm

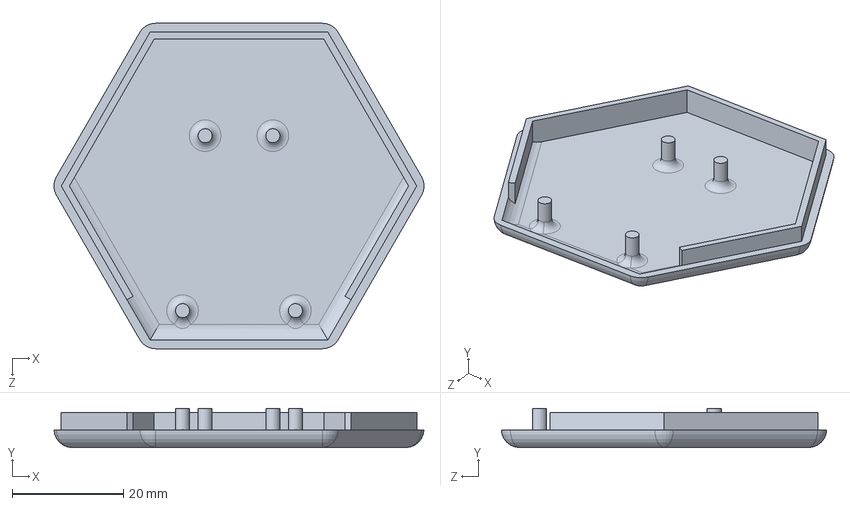
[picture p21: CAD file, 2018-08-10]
hardware/cad/tritag-case/tritag_case_top.SLDPRT
66.6 x 7.05 x 58.6 mm

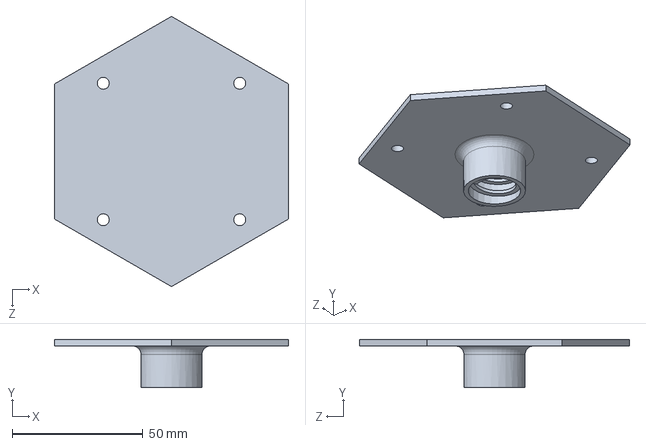
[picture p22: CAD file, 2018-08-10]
hardware/cad/polypoint-mount/staff.SLDPRT
89.3 x 18.4 x 103.2 mm

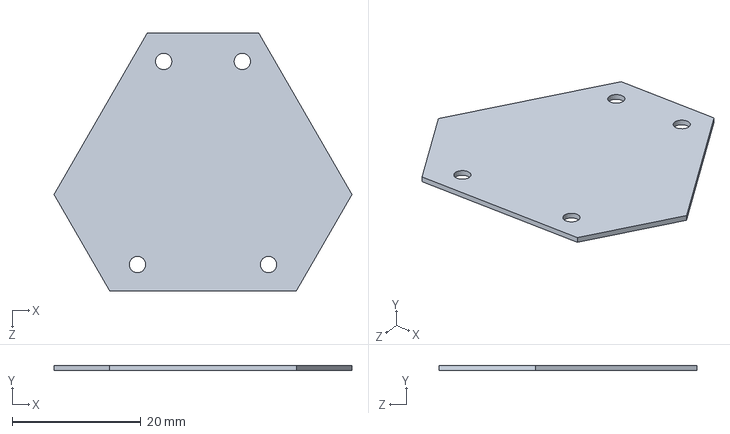
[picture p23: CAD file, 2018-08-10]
hardware/cad/tritag-board/pcb.SLDPRT
46.2 x 0.8 x 40.0 mm

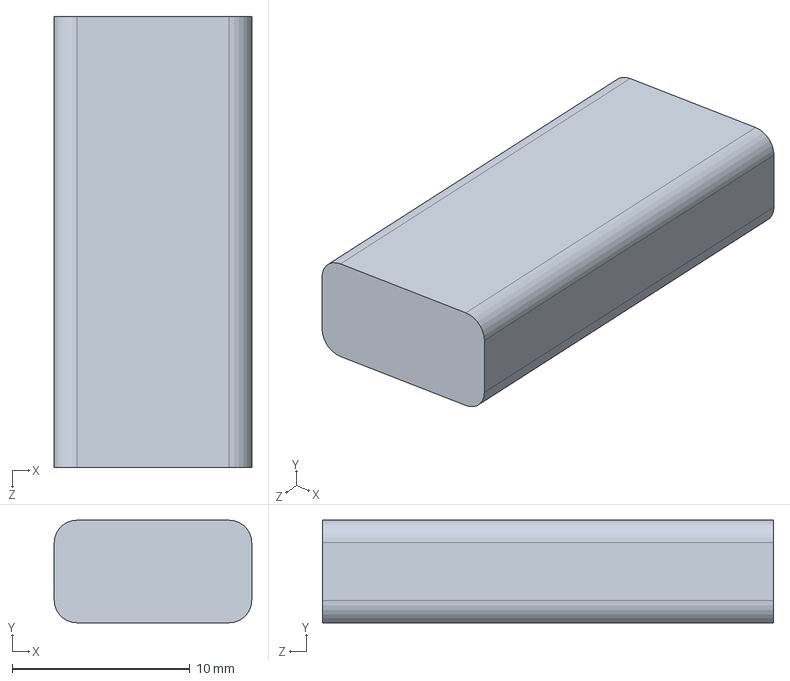
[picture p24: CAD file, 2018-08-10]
hardware/cad/tritag-board/battery_110mAh.SLDPRT
11.1 x 5.78 x 25.4 mm

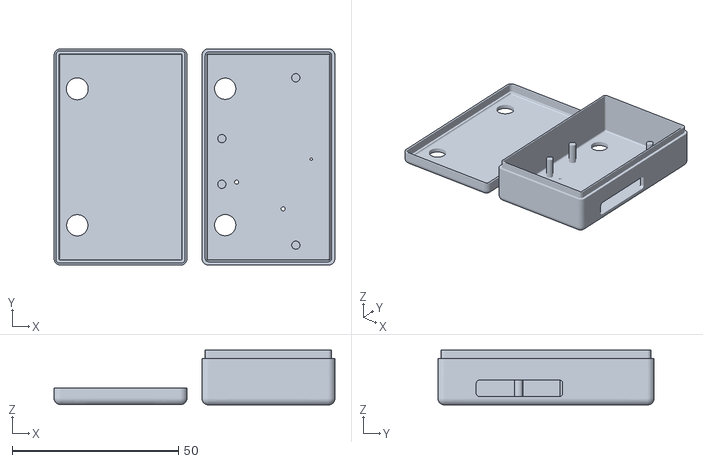
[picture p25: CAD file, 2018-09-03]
hardware/cad/tottag-case/case_v2.stl
84.4 x 65.0 x 16.5

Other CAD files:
hardware/cad/polypoint-mount/polypoint_backplate_hexagon.STL
hardware/cad/tottag-case/case_v6.stl
hardware/cad/tritag-board/outline.SLDPRT
hardware/cad/tottag-case/case_v5.stl
hardware/cad/tottag-case/case_v4.stl
hardware/cad/tottag-case/case_v3.stl
hardware/cad/tritag-board/board_2d.SLDPRT
hardware/cad/tottag-case/case.stl
hardware/cad/okw/minitec-D-L/00011824.DWG
hardware/cad/okw/minitec-D-L/00011824.dxf
hardware/cad/okw/minitec-E-L/00011818.DWG
hardware/cad/polypoint-mount/backplate_hexagon.STL
hardware/cad/polypoint-mount/staff.STL
hardware/cad/tottag-case/case.ipt
hardware/cad/tritag-case/tritag_case_bottom.STL
hardware/cad/tritag-case/tritag_case_top.STL
hardware/tottag/rev_i/rev_i v174.f3z
hardware/tottag/rev_p/rev_p.2.f3z

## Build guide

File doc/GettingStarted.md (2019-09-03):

Getting Started
===============

This document covers the basic pieces and has all the directions for software you will need.

<!-- npm i -g markdown-toc; markdown-toc -i GettingStarted.md -->

<!-- toc -->

- [Hardware Glossary](#hardware-glossary)
- [Software Glossary](#software-glossary)
- [Miscellaneous](#miscellaneous)

<!-- tocstop -->

## Hardware Glossary

These are all the major pieces of the platform and supporting development environment.
You should make sure you have all of these pieces before getting going.

<table>
  <tr><th>Name</th><th>Picture</th><th>What it is used for</th></tr>
  <tr>
    <td>TotTag</td>
    <td>
      
      
    </td>
    <td>
      <p>This is the TotTag hardware.</p>
      <p>Most of the time you should not need to worry about what parts of the
      board do what things, however it is important to pay attention to the two
      programming headers.</p>
      <p>In general, you should also try to avoid having any large amounts of
      metal near any of the antennas.</p>
      <p><strong>Note:</strong> The Device ID is just a sticker on the board.
      When the board is programmed, you manually set the ID to match this sticker.</p>
    </td>
  </tr>
  <tr>
    <td>
      <p><a href="https://www.segger.com/products/debug-probes/j-link/models/j-link-edu/">JLink Programmer</a></p>
      <p><small>Note: Link is to the EDU edition, which should be much cheaper ($60 vs $378 at time of writing)</small></p>
    </td>
    <td>
      
      
    </td>
    <td>
      <p>This is the JLink programmer. Often just the word "programmer" or "JLink" will be used, they all mean this box.</p>
      <p>Working with TotTags you may frequently have multiple JLinks plugged
      into your machine. On the back of each box is a serail number (the S/N
      part) that you can use to choose a specific programmer.</p>
    </td>
  </tr>
  <tr>
    <td>
      <p>JLink Adapter</p>
    </td>
    <td>
      
    </td>
    <td>
      <p>This is an adapter board designed by the Lab11 team.</p>
      <p>You can get <a href="http://www.tag-connect.com/adaptors">similar boards</a>
      from Tag Connect directly, but they do not have the power control or reset button.</p>
      <p><strong>Note:</strong> For TotTag the switch should <strong>always</strong>
      be in the unlabeled or down position (the top position says <tt>RST</tt>).
      <p><strong>Note:</strong> Pay attention to the power switch. If the tag is plugged into
      USB or attached to a battery, the switch should be in the <tt>DEV</tt> ("power from device")
      position. If the tag is only plugged into the programmer, it should be in the <tt>3V3</tt>
      ("3.3V from the programmer box") position.</p>
    </td>
  </tr>
  <tr>
    <td>TagConnect Cable</td>
    <td>
      <table>
        <tr>
          <td></td>
          <td rowspan="2"></td>
        </tr>
        <tr>
          <td></td>
        </tr>
      </table>
    </td>
    <td>
      <p>The <a href="http://www.tag-connect.com/TC2030-IDC-NL">TagConnect
      Cable</a> attaches the programmer to the board.</p>
      <p>For quick use, just holding the spring-loaded pins in by hand works
      well. For extended use, there is a backing board that will fix the cable
      to the board.</p>
    </td>
  </tr>
</table>

## Software Glossary

You will need to have each of these tools installed:

 - [git](https://git-scm.com/) - Version control software. Used to keep track
   of all of TotTag code and documentation.

 - [JLink Software](https://www.segger.com/downloads/jlink/#J-LinkSoftwareAndDocumentationPack) - Software
   for your computer to talk to the JLink programmer. You need to hit the
   "Click for Downloads" link under "J-Link Software and Documentation Pack".

## Miscellaneous

 - [The TotTernary Repository](https://github.com/lab11/totternary) - This
   website, where you will find all of the code and documentation for the
   platform.

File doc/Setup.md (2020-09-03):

Machine Setup
=============

This document describes how to set up a machine and programming environment for
working with TotTags.

> **Reminder:** If while you are working, you find that there was anything that
> was unclear, or there were any extra steps you had to take to get things
> working, _please update this document!_ If you are viewing this online, there
> should be a small pencil-looking icon in the top right corner that will let
> you propose edits.

---

* [Operating System](#operating-system)
* [Working in a Terminal](#working-in-a-terminal)
* [Source Control Tools](#source-control-tools)
* [Getting the Code](#getting-the-source-code)
    * [Updating the Code](#updating-the-code)
* [Getting the Compiler](#getting-the-compiler)
    * [Verify you can build firmware](#verify-you-can-build-firmware)
* [Getting Python](#getting-python)
* [Getting Node](#getting-node)
    * [Getting Noble](#getting-noble)
    * [Testing Noble](#testing-noble)
    * [Debugging Noble](#debugging-noble)
    * [Testing for TotTags](#testing-for-tottags)
* [All done!](#all-done)

---

## Operating System

The TotTag development environment assumes you have access to a Linux, Mac, or
Windows machine. Bluetooth access and reliability on Windows and Mac is quite
poor, so you may need access to a Linux machine to test Bluetooth capabilities
and to calibrate devices.

For Linux, this guide will assume you assume you are using
[Ubuntu](https://ubuntu.com/); however, other Linux distros will work just as
well.

If you want to use a virtual machine, it's most reliable to buy a
[cheap Bluetooth dongle](https://www.amazon.com/Kinivo-USB-Bluetooth-4-0-Compatible/dp/B007Q45EF4/)
and pass it through to the guest OS. This also fixes the problem of using a
cheap laptop that doesn't come with Bluetooth 4.0 built-in.

Finally, to facilitate ease of use, we provide an
[Ubuntu 18.04 LTS virtual machine](https://people.ee.ethz.ch/~abiri/projects/totternary/totternary.ova)
which has all of the necessary tools pre-installed.

Installation instructions:

1. [Download VirtualBox](https://www.virtualbox.org/wiki/Downloads).
2. Install it *with* the USB driver (will be required to connect to the SEGGER JLink).
3. Import the virtual machine.
4. Log in: **Username** *tot*, **Password** *lab11totternary*.
5. Use the 'Terminal' (left side of the screen, black box icon) to enter commands.

## Working in a Terminal

There is a program called `terminal` built into most operating systems (`cmd` on
Windows). It lets you type commands for the computer to execute. We will do all
of our work in the terminal.

If you've never used a terminal before,
[here's a decent starter guide](https://medium.com/@grace.m.nolan/terminal-for-beginners-e492ba10902a).
It's a lot faster to develop software for use in a terminal, at the expense of
that software being a bit less user-friendly.

## Source Control Tools

We use [Git](https://git-scm.com/) to manage code:

```bash
# For Ubuntu
sudo apt install git
```

## Getting the Source Code

All of the TotTag materials, including firmware, documentation, and calibration
data live in a [repository](https://github.com/lab11/socitrack). While you can
browse this online, you'll also need a local copy on your machine. You will
`clone` the repository to obtain this:

```bash
# This command will create a folder called "socitrack"
git clone --recursive https://github.com/lab11/socitrack
```

That `--recursive` bit is important. We use some other external software
libraries, and this will pull those in.

### Updating the Code

Occasionally you will need to update the code to obtain any changes in the
repository. From the `socitrack` folder that you cloned, run:

```bash
# Remember you must be inside the socitrack folder for this to work
git pull --recurse-submodules
```

## Getting the Compiler

You will need a special compiler to build code for the TotTags. Full directions
are available from
[ARM's website](https://developer.arm.com/tools-and-software/open-source-software/developer-tools/gnu-toolchain/gnu-rm/downloads),
however these are the basic directions for Linux and/or Mac:

```bash
# Go to your home directory
cd ~

# Download the toolchain
# This is reasonably large (~100 MB) and may take a moment
wget https://developer.arm.com/-/media/Files/downloads/gnu-rm/9-2020q2/gcc-arm-none-eabi-9-2020-q2-update-x86_64-linux.tar.bz2

# Decompress the toolchain (.tar.bz2 is similar to a .zip, just different format)
# You can make life easier with "tab completion", just type "tar -xf gcc<tab>"
tar -xf gcc-arm-none-eabi-8-2019-q3-update-linux.tar.bz2

# Add this new program to your PATH
# You can use any text editor, nano is very user-friendly for a text-based program
nano .bashrc

# At the bottom of the file, add this line
# Be careful to add this exactly, no extra spaces, and don't miss quotes
PATH="$PATH:$HOME/gcc-arm-none-eabi-9-2020-q2-update/bin/"

# Press Ctrl-X to exit nano, type Y for yes to save, and enter to accept the
# file name.
```

There is also a Windows version of the compiler available from the same site.
It comes with an installer that can be used in place of the above commands.
After installation, everything works exactly the same regardless of the
Operating System.

Now, **open a new terminal**, and verify that the compiler is set up correctly
by trying to run the compiler. Here's the result on my machine:

    ppannuto@ubuntu:~$ arm-none-eabi-gcc --version
    arm-none-eabi-gcc (GNU Tools for Arm Embedded Processors 9-2019-q4-major) 9.2.1 20191025 (release) [ARM/arm-9-branch revision 277599]
    Copyright (C) 2019 Free Software Foundation, Inc.
    This is free software; see the source for copying conditions.  There is NO
    warranty; not even for MERCHANTABILITY or FITNESS FOR A PARTICULAR PURPOSE.

### Verify you can build firmware

```bash
cd socitrack/software/squarepoint
make ID=c0:98:e5:42:00:FF
# ... hopefully lots of output, ending something like this:
arm-none-eabi-objcopy -Obinary _build/squarepoint.elf _build/squarepoint.bin
arm-none-eabi-size _build/squarepoint.elf
   text	   data	    bss	    dec	    hex	filename
  44076	    344	   9728	  54148	   d384	_build/squarepoint.elf
# it's fine if the exact numbers vary a little
```

## Getting Python

_Note: Python is only used during calibration. If you won't need to calibrate any nodes, you can skip this._

If you have a brand new machine, you'll need to install Python. Windows versions
of Python can be downloaded and installed from the
[Python website](https://www.python.org/downloads/). Linux users can install
Python using the following:

```bash
sudo apt install python3
```

And verify it's installed:

```bash
pannuto@ubuntu:~$ python3 --version
Python 3.7.3
# Exact versions may vary
```

### Getting Python Dependencies

The package manager for Python does not come with the Python installation on
Linux machines, so you may need to install that as well:

    sudo apt install python3-pip

Then we need to use `pip3` to install some python packages that tools will use
on all Operating Systems:

    pip3 install dataprint numpy matplotlib future

## Getting Node

Node is a program that runs JavaScript code as programs. We recommend installing
the latest Long-Term Support release of node (v12.18.3) using [NVM](http://nvm.sh),
the "Node Version Manager":

```
wget -qO- https://raw.githubusercontent.com/nvm-sh/nvm/v0.35.3/install.sh | bash
nvm install v12.18.3
```

On Windows, you can install NVM from this
[link](https://github.com/coreybutler/nvm-windows/releases/download/1.1.7/nvm-setup.zip),
after which you should open a terminal and enter:

```
nvm install 12.18.3
nvm use 12.18.3
```

If everything worked, you should be able to run:

    ppannuto@ubuntu:~$ node --version
    v12.18.3
    # It is okay if this is a different version

#### Getting Noble

At this point you can try installing Noble, a Node library that enables us to 
communicate with Bluetooth LE devices. Head to the calibration folder:

    cd software/tottag/calibration
    npm install

This will produce a lot of text, hopefully none of it says `ERR!` anywhere:

    gyp ERR! build error

Warnings are fine:

    npm WARN notsup SKIPPING OPTIONAL DEPENDENCY: Unsupported platform for xpc-connection@0.1.4: wanted {"os":"darwin","arch":"any"} (current: {"os":"linux","arch":"x64"})

If Noble doesn't install, you have some debug work to do. This is a good point
to reach out for more help.

As Bluetooth can interact with the outside world, it's treated as a potential
security risk. On Linux or Mac, you need to give Node permission to use Bluetooth.
You should only need to do this once:

    sudo setcap cap_net_raw+eip $(eval readlink -f `which node`)

#### Testing Noble

Still in the debug folder:

    ppannuto@ubuntu:~/totternary/software/debug$ node test_noble.js 
    ** TotTag -- Noble test
    **
    ** Any Bluetooth advertisement seen is printed. Press Ctrl-C to exit at any time.

    Scanning...
    Found: RISE209
    Found: undefined
    Found: RISE94
    Found: LHB-BB47EDCC
    Found: undefined
    Found: undefined
    Found: undefined
    Found: LHB-8D37A6E1

It usually takes a few seconds for the first device to show up. While it's
possibly that there are no Bluetooth devices around, it's pretty unlikely
nowadays, so something should print.

#### Debugging Noble

Bluetooth is unfortunately kind of finicky, so here are some issues:

##### Powered Off

Occasionally, Noble will print a message about being powered off, like this:

    ppannuto@ubuntu:~/totternary/software/debug$ node test_tags_visible.js
    ** TotTag -- Bluetooth test
    **
    ** Each TotTag seen via Bluetooth will print. Press Ctrl-C to exit at any time

    Scanning...
    Found TotTag: c0:98:e5:42:00:25
    WARNING: Tried to start scanning, got: poweredOff

If this happens, simply kill the script and start it again.

##### Permissions

If at any point you see this message

    noble warning: adapter state unauthorized, please run as root or with sudo
                   or see README for information on running without root/sudo:
                   https://github.com/sandeepmistry/noble#running-on-linux

It means you need to run the permission step:

    sudo setcap cap_net_raw+eip $(eval readlink -f `which node`)

#### Testing for TotTags

If you happen to have a programmed TotTag around, you can try looking
for just that device:

    ppannuto@ubuntu:~/totternary/software/debug$ node test_tags_visible.js
    ** TotTag -- Bluetooth test
    **
    ** Each TotTag seen via Bluetooth will print. Press Ctrl-C to exit at any time

    Scanning...
    Found TotTag: c0:98:e5:42:f0:06

Each TotTag will print only once. The ID printed should match the sticker on the
back of the device.

---

## All done!

This should be everything you need to install.

The next step is [Provisioning!](Provisioning.md)

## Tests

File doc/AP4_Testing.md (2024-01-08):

Testing
============

## Run tests on Apollo4 based TotTags

### Flash the boards
1. Navigate to the test folder

        cd socitrack/software/firmware/tests

2. Clean up the old builds

        make clean
3. Program the device ID (using `ff` as an example here)

        make ID=c0:98:e5:42:00:ff UID
4. Program the test firmware (available BOARD_REV for apollo4 based TotTag: `EVB`, `I`, `K`, `L`, see the revision letter on the side of the TotTag name on the board; for the list of available tests, see the makefile)
```bash
#test individual peripheral
make ranging_radio BOARD_REV=EVB
#test the full app
make full BOARD_REV=M
```

### Debug the boards

#### Read real-time SWO output
With the JLink debugger connected, run the following command.

        jLinkSWOViewerCL -swoattach 1 -swofreq 1000000 -device AMA4B2KP-KBR -itmport 0x0

You should be seeing the debugging messages coming after that.

#### Resetting the device without restarting

        JLinkExe -Device AMA4B2KP-KBR -if SWD -speed 4000 -RTTTelnetPort 9201

Then in the JLink interface, use command `r` and `g` to reset the device.

When the device is reset without restarting, the RTC value would not get lost.

#### GDB based debugging
1. In one terminal tab, run the following command to start the GDB server

        JLinkGDBServer -if swd -device AMAP42KK-KBR -endian little -speed 1000 -port 2331 -swoport 2332 -telnetport 2333 -RTTTelnetport 2334 -vd -ir -localhostonly 1 -singlerun -strict -timeout 0

2. In another terminal tab, navigate to the `bin` folder with the compiled files

        cd socitrack/software/firmware/tests/bin

3. invoke the GDB debugger

        arm-none-eabi-gdb

4. With the GDB debugger starting, load the `.axf` file and start the test

        file TestRangingRadio.axf
        target remote localhost:2331
        load
        mon reset 0

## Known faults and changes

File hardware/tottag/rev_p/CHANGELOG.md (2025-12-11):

# Changes for Rev P.2

 - Update DRC per MF request
   - Min annular ring 2mil -> 3mil
   - Min spacings (via-X) 4mil -> 3mil
   - Nudge handful of components, vias, wires as-required for new DRC

# Changes from Rev O

 - Update sch with explicit NC pins
    - Fusion now supports marking pins are not-connected; use that.
 - Add back test points for USB SPI lines
 - Workaround for ERR125 (Apollo4 VDDB rise time)
    - Create dedicated `AP4_VDDB_SUP` net
    - Double the decap to (loosely) double local RC constant
 - Remove `RZ4` (replace with wire)
    - (was hedge for UWB LNA `VDD` supply)
 - Remove `RZ3`,`RZ5` (replace with `SJ9`,`SJ10`)
    - (was hedge for USB power rails to AP4)
    - Probably could remove SJ's too, but plenty of real estate, and still a
      newer / comparatively unstressed facet, and AP4 USB has lots of errata
 - Rename:
    - `RZ1 --> RZ2`, `RZ2 --> RZ3` (on chopping block, and now match supply)
    - `RZ6 --> RZ1` (change to 1 b/c most long-term part likely)
    - Fix capacitor ordering
 - Replace `C17` on AP4 !RST with same BOM line item as `C14-16`
    - Don't need the higher grade cap here, but cuts a one-off component
 - Replace `C58` (buzzer decap) with majority 0201 1µF BOM item
 - Replace `C59` (QI AD decap) with majority 0201 1µF BOM item
 - Replace `C60,C61` (BQ24040 IN,OUT decap) with majority 0201 1µF BOM item
 - Update stackup to match the standard 4-lay, 0.8 thick from MacroFab

## Hedges not yet removed

 - `SJ9`, `SJ10` (USB power supply; remove soon)
 - `RZ2`, `RZ3` (DW VDD2, VDD3 supply; remove soon)
 - `RZ1` (AP4 BLE RF supply; matches EVB; never used, could likely remove)

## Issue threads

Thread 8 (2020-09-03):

### ISSUE TITLE
SW: Pin reconfigurations for Rev G

### ISSUE THREAD

**Issue by ppannuto** [lab11/socitrack#8]
Some of the pins for the nrf updated from Rev F to Rev G. I tried to make sure that nothing _bad_ would happen if old rev software runs, but the one risk is the `BUZZER_GATE`, which is floating and might burn out the speaker if not pulled off. That was an unconnected pin before, so it's safe to change that in the Rev F firmware as well such that the speaker is simply always controlled.

**Revision G:**
<img width="720" alt="image" src="https://user-images.githubusercontent.com/339422/86535766-b9dcd380-beb0-11ea-9b27-6445b6efea01.png">

**Revision F:**
<img width="649" alt="image" src="https://user-images.githubusercontent.com/339422/86536074-c5c99500-beb2-11ea-964d-ca6ece3084d8.png">

---

## Changed Pin List

(You should probably double-check me, just in case :) )

 - [x] USB pins now connected
 - [x] `LED_NRF_GREEN` `P0.06` -> `P1.05`
 - [x] `DBG_RX` removed (was FTDI UART)
 - [x] `DBG_TX` removed (was FTDI UART)
 - [x] `!SD_DETECT` `P1.00` -> `P0.11`
 - [x] `LED_NRF_BLUE` `P0.04` -> `P1.07`
 - [x] `LED_NRF_RED` `P0.05` -> `P1.04`
 - [x] (new) `!CHG` `P1.02` -- "Low (FET on) indicates charging and OpenDrain (FET off) indicates no Charging or Charge complete."
 - [x] (new) `!PG` `PXXX` -- "Low (FET on) indicates the input voltage is above UVLO and the OUT (battery) voltage."
    - From https://www.ti.com/lit/ds/symlink/bq24040.pdf?ts=1593963502813&ref_url=https%253A%252F%252Fwww.ti.com%252Fproduct%252FBQ24040
 - [x] `!FT_RST` removed (was FTDI reset signal)
 - [x] (new) `BUZZER_GATE` `P1.15` -- Drives a PFET that drives a buzzer. **Must be pulled high to default buzzer off.** This was intentionally put on an unconnected pin in prior revisions, so all firmware should drive this pin to ensure it isn't accidentally floated. Should be driven with a PWM signal to drive buzzer.
 - [x] (new) `QI_TS_CTRL` `P0.25` -- `TS/CTRL` pin of [bq51013B](https://www.ti.com/lit/ds/symlink/bq51013b.pdf?HQS=TI-null-null-digikeymode-df-pf-null-wwe&ts=1593963941247), see §7.3.14 for details. Used to signal charge complete to wireless charger.

**Comment by ppannuto** [comment]
Buzzer details:

<img width="254" alt="image" src="https://user-images.githubusercontent.com/339422/86536511-3920d600-beb6-11ea-9dad-00856ac8e496.png">

http://www.puiaudio.com/pdf/SMT-0440-T-2-R.pdf

**Comment by hedgecrw** [comment]
All changes implemented with latest push

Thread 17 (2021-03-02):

### ISSUE TITLE
SW: RTC and timezones

### ISSUE THREAD

**Issue by ppannuto** [lab11/socitrack#17]
I spent a minute trying to figure out how one of my nodes had gotten three hours off today, only to eventually put together that it was indeed 10:20 US/Pacific... I'm not sure what exactly the best policy is here, but I think it makes sense to program the RTC on the board with UTC time as programming the RTC is ideally rare and could happen anywhere, so that should be globally consistent.

We should probably add something to the data processing as well, but I think "which time zone was this device in while recording" is more of a metadata problem.

**Comment by hedgecrw** [comment]
This has been resolved with the latest check-in.

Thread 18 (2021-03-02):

### ISSUE TITLE
SW: Logfile name always DATA.LOG

### ISSUE THREAD

**Issue by ppannuto** [lab11/socitrack#18]
Since we're defaulting to `DISABLE_RTC_TIME_CHECK`, the logger doesn't try to use time at all, and will name the logfile `DATA.LOG` even if the device does have a valid timestamp.

**Comment by hedgecrw** [comment]
This is fixed with the latest check-in. Now it works like so:

If the RTC time is valid at boot, it will automatically create the time-based log file. If it is not valid, it will create a file named ID@DATA.LOG. In the future, once a valid RTC time is acquired by the network, a new log file will be created with the correct time-based name.

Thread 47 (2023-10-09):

### ISSUE TITLE
SW: Rev M — Updated connection information (since rev L)

### ISSUE THREAD

**Issue by ppannuto** [lab11/socitrack#47]
There is no more `LED2`, there is only `LED1_{RED,GREEN}`. The `LED1` pins are unchanged.

DWM1:
 - `!SPI_CS` — `GP29` (same)
 - `!RST` — `GP50` (same)
 - `WAKEUP` — `GP26` (same)
 - `IRQ` — `GP27` (same)

DWM2:
 - `!SPI_CS` — `GP24` (same)
 - `!RST` — `GP82` **!! This pin is also `SWTRACE2` on the AP4BP module.***
 - `WAKEUP` — `GP63`
 - `IRQ` — `GP72`

DWM3:
 - `!SPI_CS` — `GP25` (same)
 - `!RST` — `GP83` **!! This pin is also `SWTRACE3` on the AP4BP module.***
 - `WAKEUP` — `GP88`
 - `IRQ` — `GP76`

*We aren't using the SWTRACE, and I ran out of GPIOs I could reasonably escape from the BGA, so I reused these two. If we do ever enable SWTRACE to debug something, need to remove `RZ2` and `RZ3` to avoid resetting DWM2 and DWM3 all the time [can use empty `RX2` and `RX3` pads to tie them to the DWM1 `!RST`]

**Comment by hedgecrw** [comment]
Done.

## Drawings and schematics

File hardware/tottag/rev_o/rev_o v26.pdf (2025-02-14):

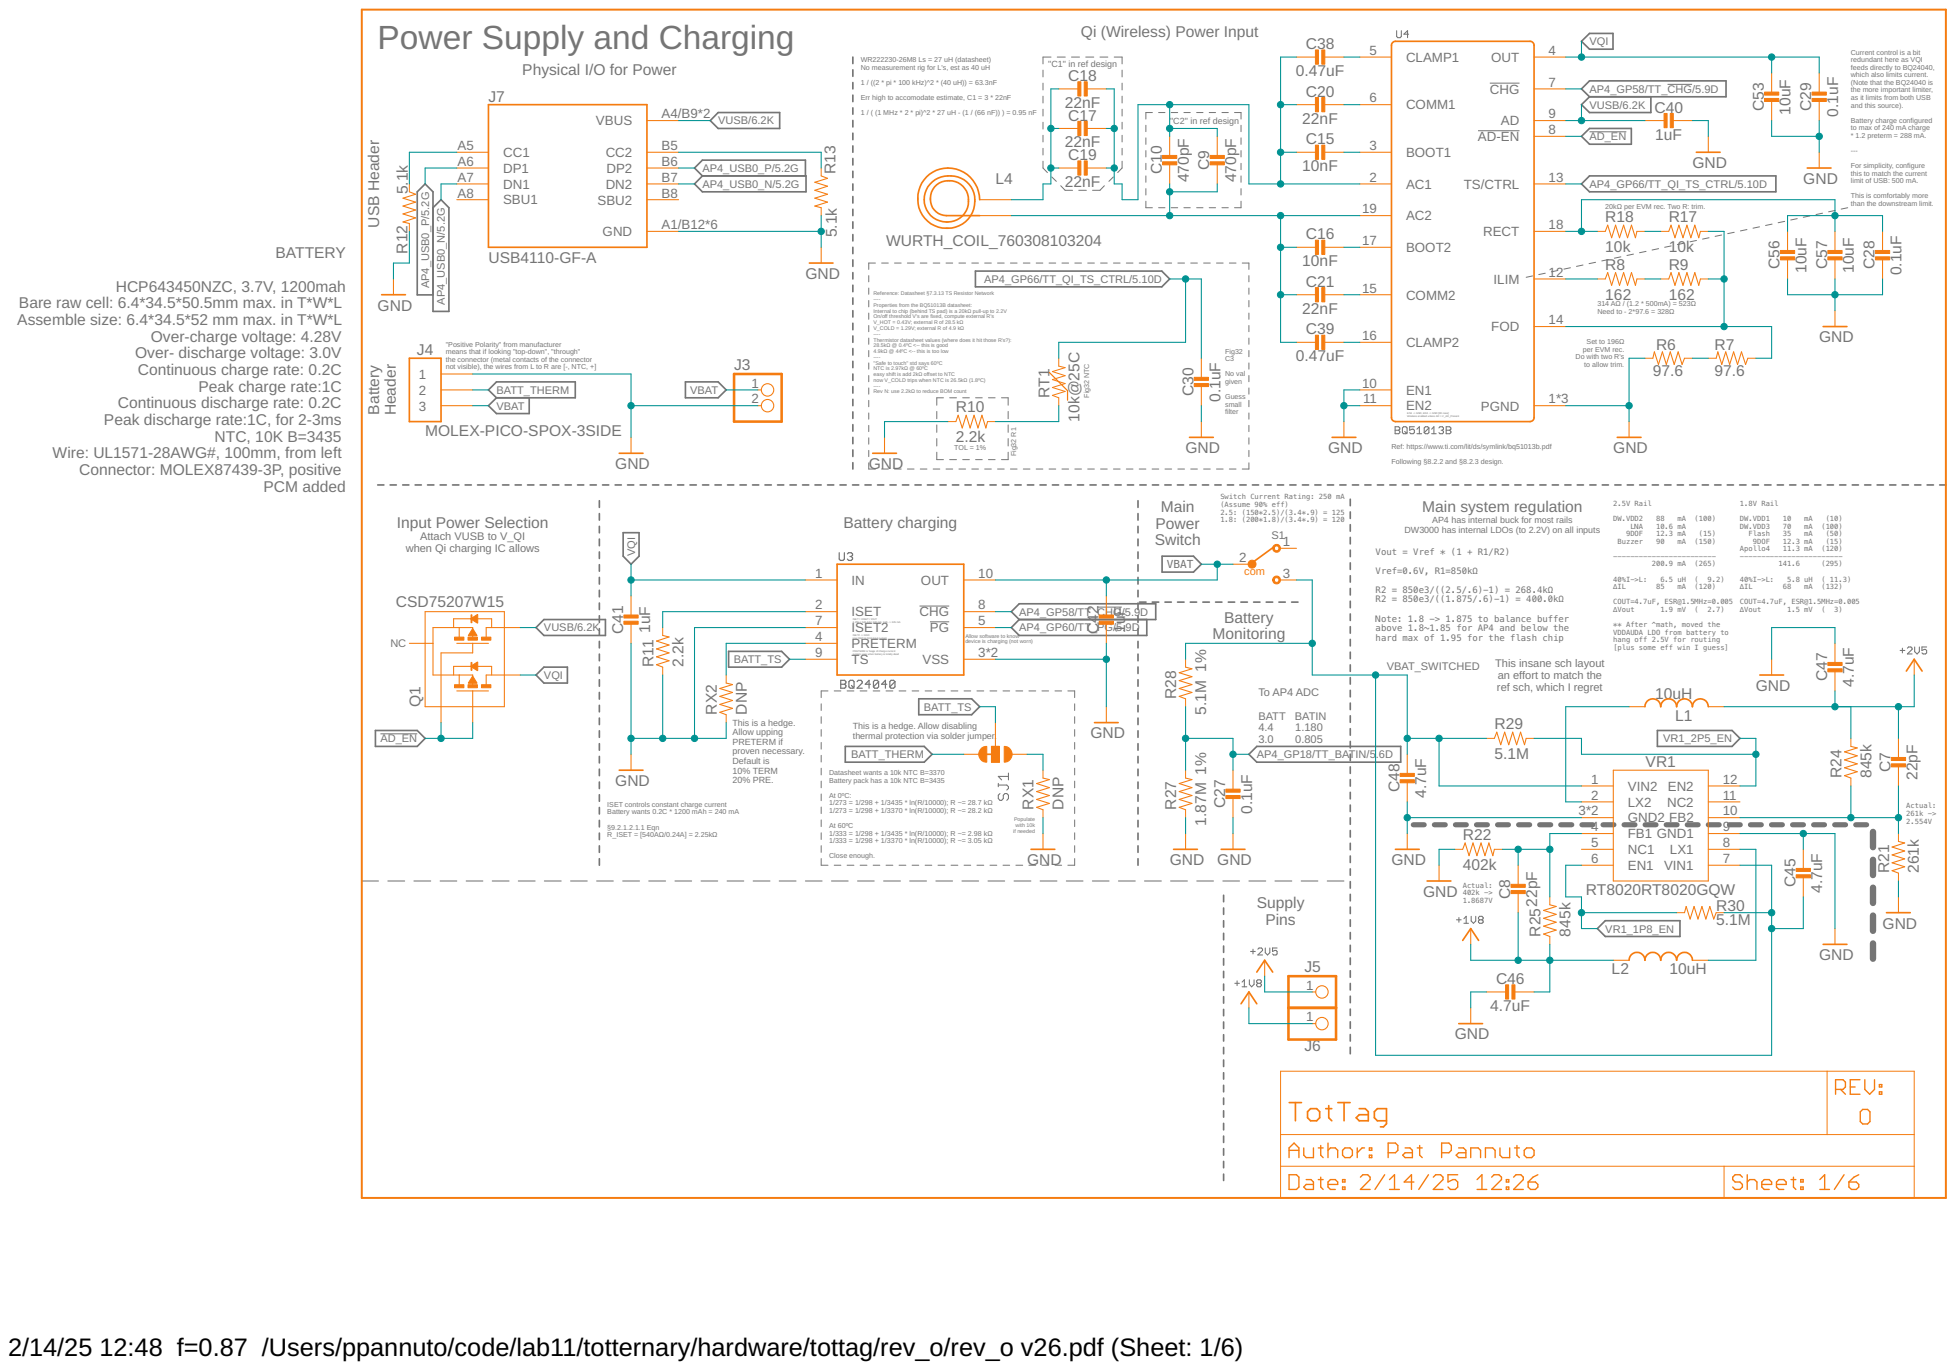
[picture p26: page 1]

Power Supply and Charging

Qi (Wireless) Power Input

WR222230-26M8 Ls = 27 uH (datasheet) No measurement rig for L's, est as 40 uH

Current control is a bit redundant here as VQI

1 / ((2 * pi * 100 kHz)^2 * (40 uH)) = 63.3nF Err high to accomodate estimate, C1 = 3 * 22nF

feeds directly to BQ24040, which also limits current. (Note that the BQ24040 is

the more important limiter, as it limits from both USB

1 / ( (1 MHz * 2 * pi)^2 * 27 uH - (1 / (66 nF)) ) = 0.95 nF

and this source). Battery charge configured

to max of 240 mA charge
* 1.2 preterm = 288 mA. --- For simplicity, configure

USB Header Battery Header
L4 WURTH_COIL_760308103204 R12

this to match the current
limit of USB: 500 mA. This is comfortably more

than the downstream limit.

20kΩ per EVM rec. Two R: trim.

BATTERY HCP643450NZC, 3.7V, 1200mah Bare raw cell: 6.4*34.5*50.5mm max. in T*W*L Assemble size: 6.4*34.5*52 mm max. in T*W*L Over-charge voltage: 4.28V Over- discharge voltage: 3.0V Continuous charge rate: 0.2C

Reference: Datasheet §7.3.13 TS Resistor Network
---- Properties from the BQ51013B datasheet:
Internal to chip (behind TS pad) is a 20kΩ pull-up to 2.2V On/off threshold V's are fixed, compute external R's V_HOT = 0.43V; external R of 28.5 kΩ

"Positive Polarity" from manufacturer means that if looking "top-down", "through"
GND MOLEX-PICO-SPOX-3SIDE

V_COLD = 1.29V; external R of 4.9 kΩ
---- Thermistor datasheet values (where does it hit those R's?): 28.5kΩ @ 0.4ºC <-- this is good

Set to 196Ω
per EVM rec. Do with two R's

the connector (metal contacts of the connector not visible), the wires from L to R are [-, NTC, +]

4.9kΩ @ 44ºC <-- this is too low
---- "Safe to touch" std says 60ºC
NTC is 2.97kΩ @ 60ºC
easy shift is add 2kΩ offset to NTC
now V_COLD trips when NTC is 26.5kΩ (1.8ºC)
---- Rev N: use 2.2kΩ to reduce BOM count

Fig32 C3 No val given Guess

EN1 -> GND, EN2 -> GND [00 case] Wireless enabled unless AD > V_AD_Present Ref: https://www.ti.com/lit/ds/symlink/bq51013b.pdf Following §8.2.2 and §8.2.3 design. Main system regulation Battery Monitoring

Attach VUSB to V_QI when Qi charging IC allows

AP4 has internal buck for most rails DW3000 has internal LDOs (to 2.2V) on all inputs

Vout = Vref * (1 + R1/R2)
Vref=0.6V, R1=850kΩ
Note: 1.8 -> 1.875 to balance buffer
above 1.8~1.85 for AP4 and below the
hard max of 1.95 for the flash chip

COUT=4.7uF, ESR@1.5MHz=0.005
** After ^math, moved the
VDDAUDA LDO from battery to
hang off 2.5V for routing
[plus some eff win I guess]

device is charging (not worn)

This insane sch layout an effort to match the
ref sch, which I regret

This is a hedge. Allow upping PRETERM if proven necessary. Default is 10% TERM

This is a hedge. Allow disabling
thermal protection via solder jumper.
BATT_THERM

Datasheet wants a 10k NTC B=3370 Battery pack has a 10k NTC B=3435 At 0ºC: 1/273 = 1/298 + 1/3435 * ln(R/10000); R ~= 28.7 kΩ

ISET controls constant charge current Battery wants 0.2C * 1200 mAh = 240 mA

2/14/25 12:48 f=0.87 /Users/ppannuto/code/lab11/totternary/hardware/tottag/rev_o/rev_o v26.pdf (Sheet: 1/6)

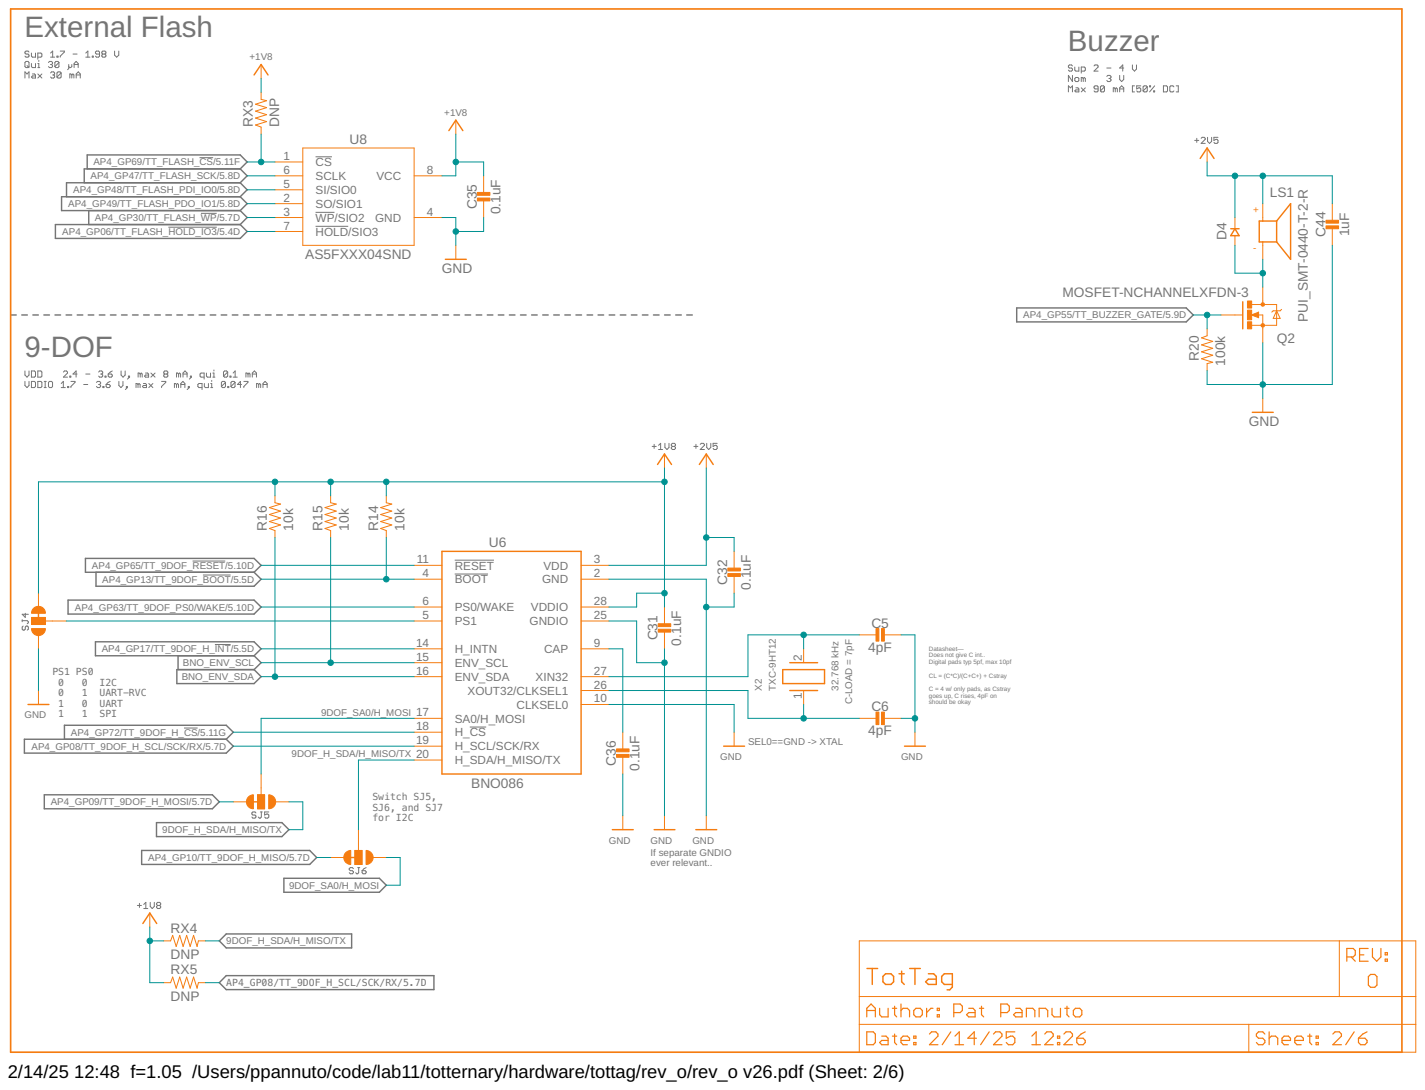
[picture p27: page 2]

Datasheet—
Does not give C int.. Digital pads typ 5pf, max 10pf CL = (C*C)/(C+C+) + Cstray C = 4 w/ only pads, as Cstray goes up, C rises, 4pF on

should be okay SEL0==GND -> XTAL

2/14/25 12:48 f=1.05 /Users/ppannuto/code/lab11/totternary/hardware/tottag/rev_o/rev_o v26.pdf (Sheet: 2/6)

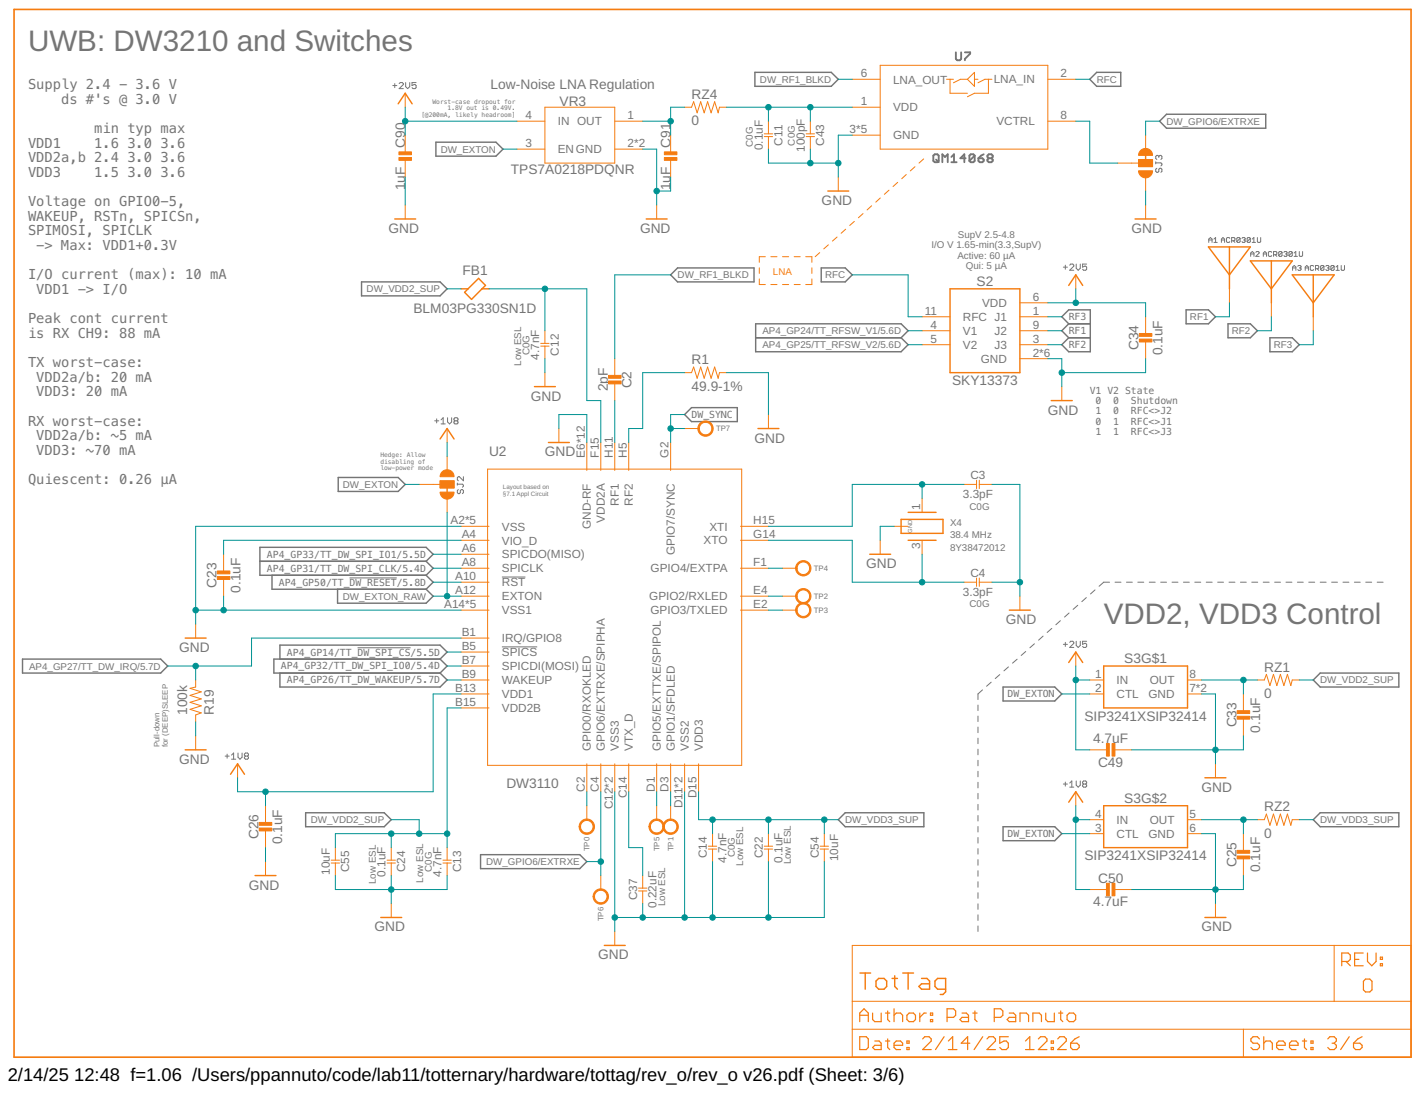
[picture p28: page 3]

Low-Noise LNA Regulation

Worst-case dropout for
1.8V out is 0.49V.

SupV 2.5-4.8
I/O V 1.65-min(3.3,SupV) Active: 60 µA Qui: 5 µA

GND-RF E6*12 RF2 H5 RF1 H11 XTI H15 XTO
GND

2/14/25 12:48 f=1.06 /Users/ppannuto/code/lab11/totternary/hardware/tottag/rev_o/rev_o v26.pdf (Sheet: 3/6)

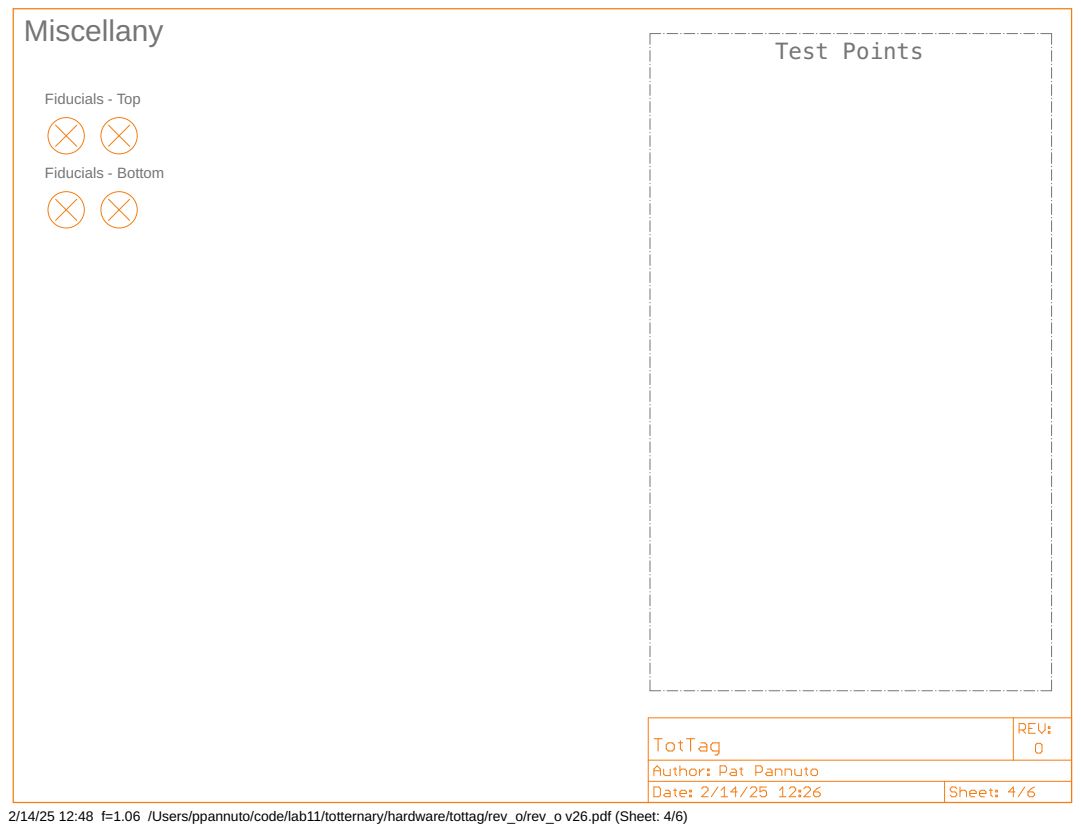
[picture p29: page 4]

2/14/25 12:48 f=1.06 /Users/ppannuto/code/lab11/totternary/hardware/tottag/rev_o/rev_o v26.pdf (Sheet: 4/6)

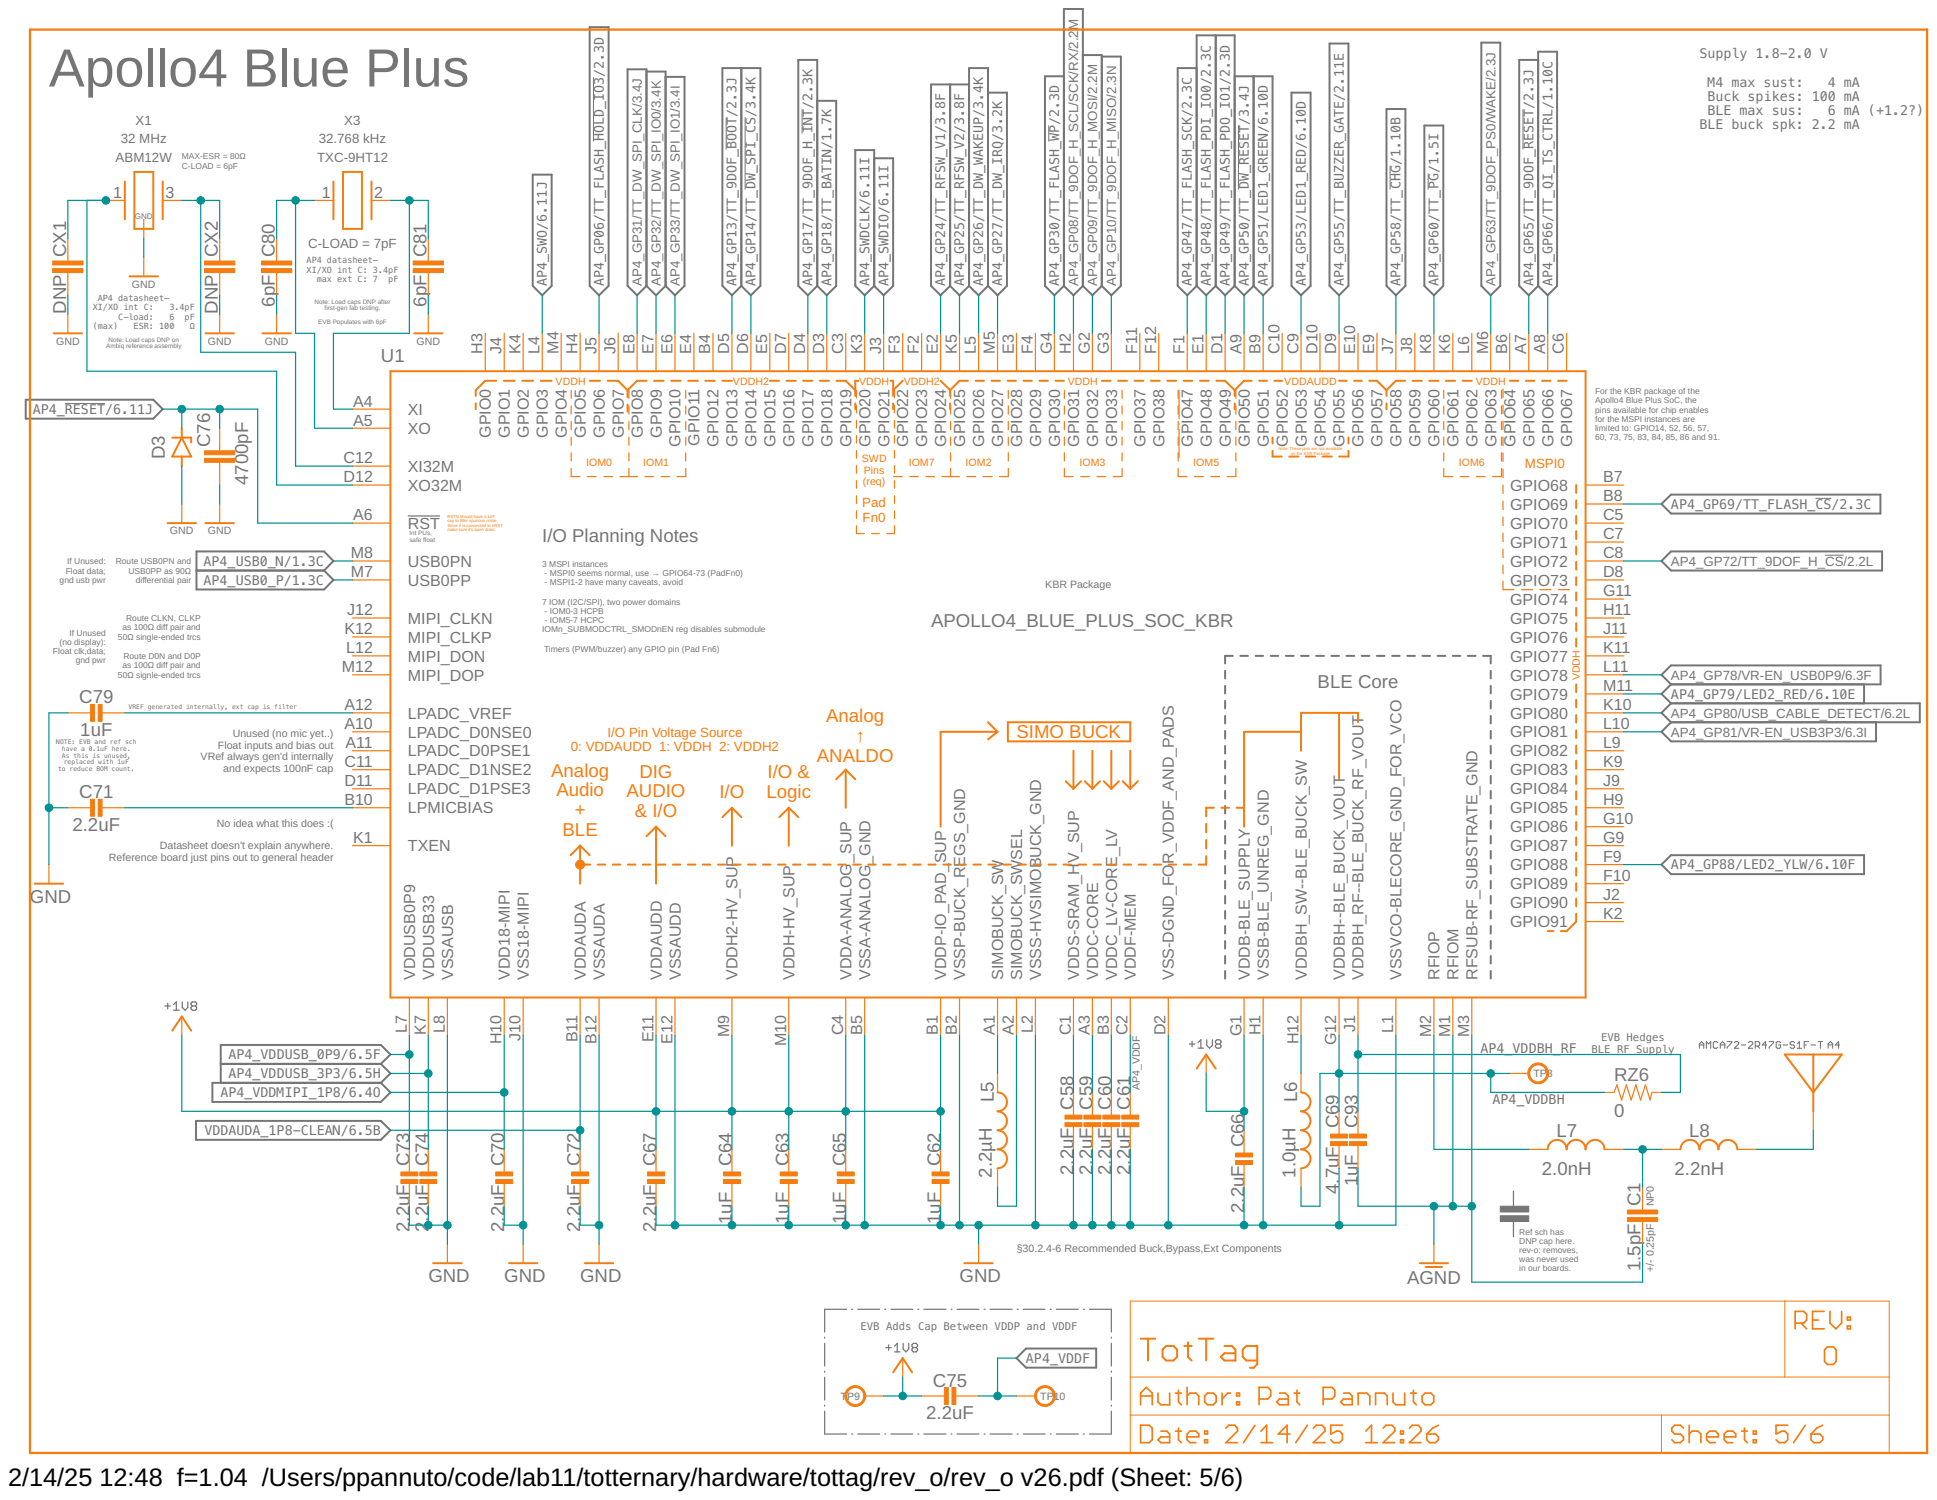
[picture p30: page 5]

Supply 1.8-2.0 V
Buck spikes: 100 mA
BLE buck spk: 2.2 mA

Note: Load caps DNP after
first-gen fab testing. EVB Populates with 6pF

Note: Load caps DNP on Ambiq reference assembly

For the KBR package of the Apollo4 Blue Plus SoC, the

pins available for chip enables
for the MSPI instances are
limited to: GPIO14, 52, 56, 57, 60, 73, 75, 83, 84, 85, 86 and 91.

Note: These pins are not available
on the KXR Package

Int PUs, safe float If Unused: Float data; gnd usb pwr

RSTN should have a 1nF
cap to filter spurious noise. Since it is connected to nRST make sure it’s open drain.
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

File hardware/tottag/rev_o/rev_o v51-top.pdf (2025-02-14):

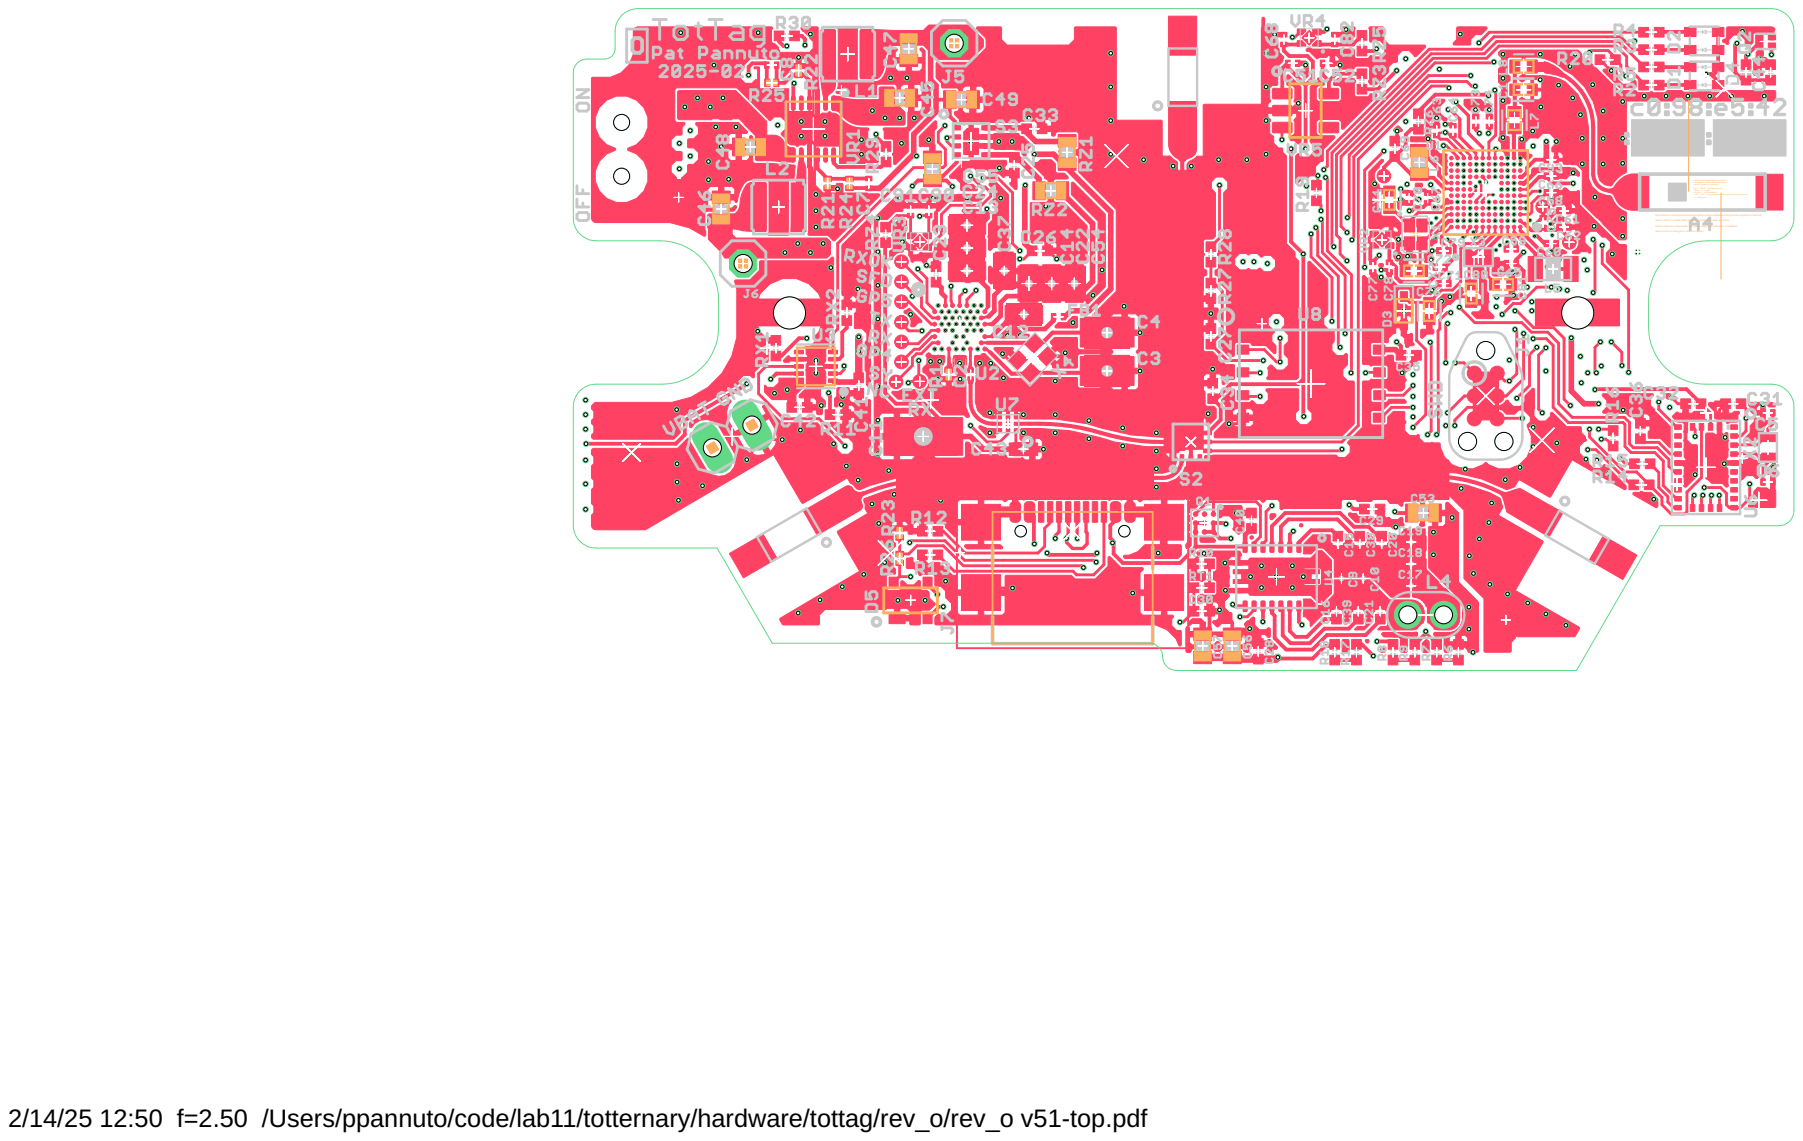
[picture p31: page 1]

Nordic forums suggest higher parasitics
if waveguide is made with internal layers, so block copper on inner layers. Trace width calc's for coplanar wave: 28 mil Conductor W

59 mil (1.6 mm) Conductor H
4 mil Conductor Gap [must match DW traces for single plane pour] ~= 49.999 ohm

https://abracon.com/uploads/resources/AMCA-Series-Multilayer-Chip-Antenna-Application-Note.pdf Goal is 10mm no-metal width, antenna in center (doc lines are 5mm) Goal is 14mm no-metal length, from plane edge (goes off board, no problem) Seems to be no feed gap in reference design

2/14/25 12:50 f=2.50 /Users/ppannuto/code/lab11/totternary/hardware/tottag/rev_o/rev_o v51-top.pdf

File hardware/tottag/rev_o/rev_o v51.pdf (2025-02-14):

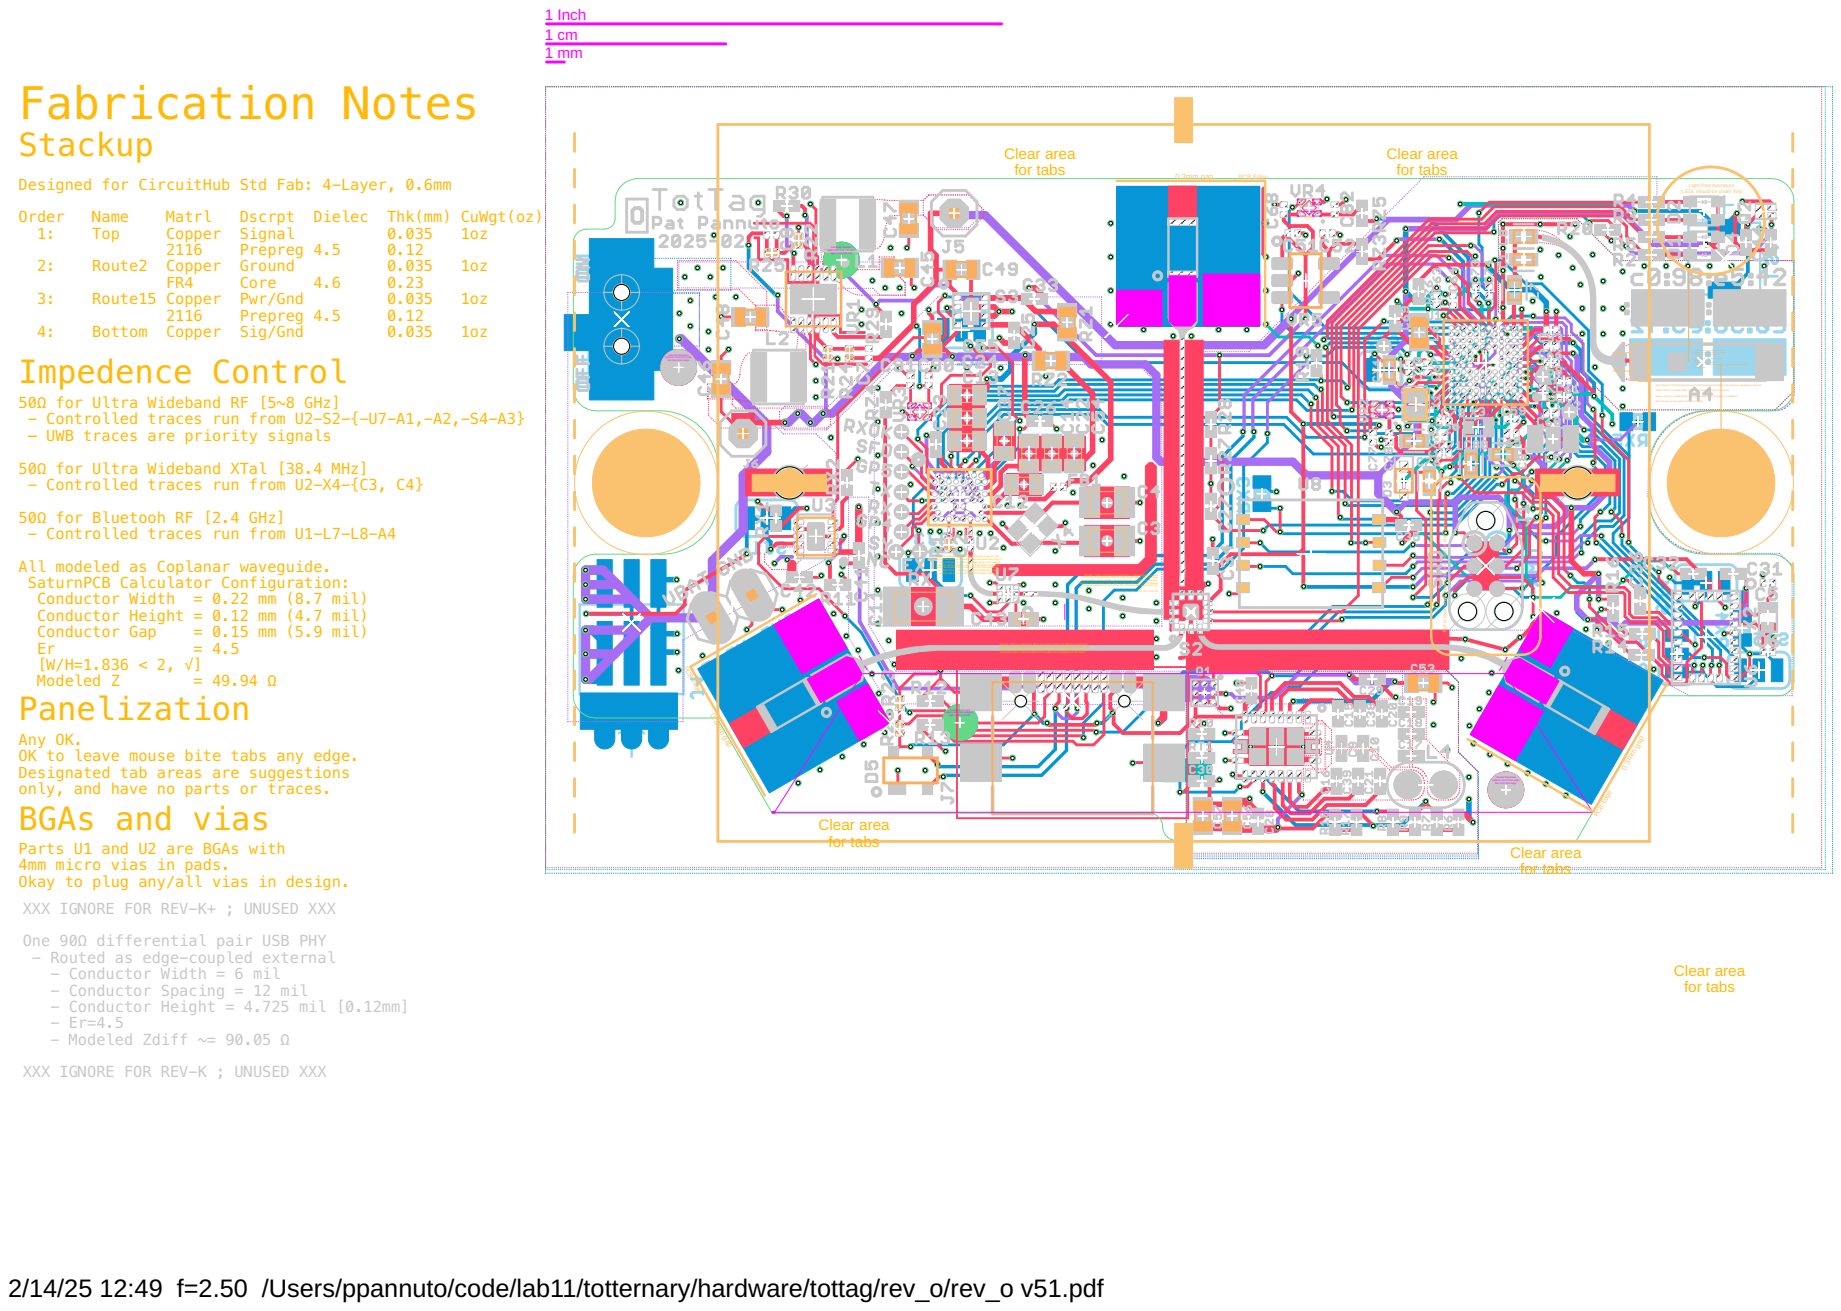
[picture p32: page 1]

Designed for CircuitHub Std Fab: 4-Layer, 0.6mm
Impedence Control

Odd land pattern. Explicit metal under solder mask. Cream is an estimate.

Fiducial Placement Optimal ~5mm from edge Min 3mm from edge

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

50Ω for Ultra Wideband RF [5~8 GHz]
- Controlled traces run from U2-S2-{-U7-A1,-A2,-S4-A3}
— UWB traces are priority signals
50Ω for Ultra Wideband XTal [38.4 MHz]
- Controlled traces run from U2-X4-{C3, C4}
50Ω for Bluetooh RF [2.4 GHz]
- Controlled traces run from U1-L7-L8-A4
All modeled as Coplanar waveguide.
SaturnPCB Calculator Configuration:
Conductor Width = 0.22 mm (8.7 mil)
Conductor Height = 0.12 mm (4.7 mil)
Panelization

Ref is main shaft; need this much lateral clearance vertically

The ground copper should be removed from under the chip
in the areas shown in the picture (Top layer and Inner Layer 1). The first solid ground copper should be on the Inner Layer 2.

If different stack-up will be used – this first solid copper layer should be at least 0.25 mm away from the Top Layer, any

inner layers close to the Top Layer should have the ground
removed in the same manner as in Inner Layer 1 above.

APH301: Place vias joining ground planes on adjacent layers around
the border of transmission lines to shield the RF signal. This technique
is sometimes called ‘stitching’ or ‘picket fencing’. The distance between
adjacent vias should be small relative to the wavelength (λ) of the highest
frequency signal on the RF trace. The recommended distance is λ/20. (c / 8 ghz) / 20 = 1.837 mm (73.8 mil)

APH301: Remove soldermask above transmission lines. It is difficult to control the
uniformity of the soldermask thickness which can result in impedance variation. Use
thin strips of soldermask at the ends of the transmission line where they connect to
component pads to prevent solder from the pads from spreading over the tracks.

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

Parts U1 and U2 are BGAs with
4mm micro vias in pads.
Okay to plug any/all vias in design.
XXX IGNORE FOR REV-K+ ; UNUSED XXX
One 90Ω differential pair USB PHY
- Routed as edge-coupled external
- Conductor Width = 6 mil
- Conductor Spacing = 12 mil
- Conductor Height = 4.725 mil [0.12mm]
- Modeled Zdiff ~= 90.05 Ω
XXX IGNORE FOR REV-K ; UNUSED XXX

2/14/25 12:49 f=2.50 /Users/ppannuto/code/lab11/totternary/hardware/tottag/rev_o/rev_o v51.pdf

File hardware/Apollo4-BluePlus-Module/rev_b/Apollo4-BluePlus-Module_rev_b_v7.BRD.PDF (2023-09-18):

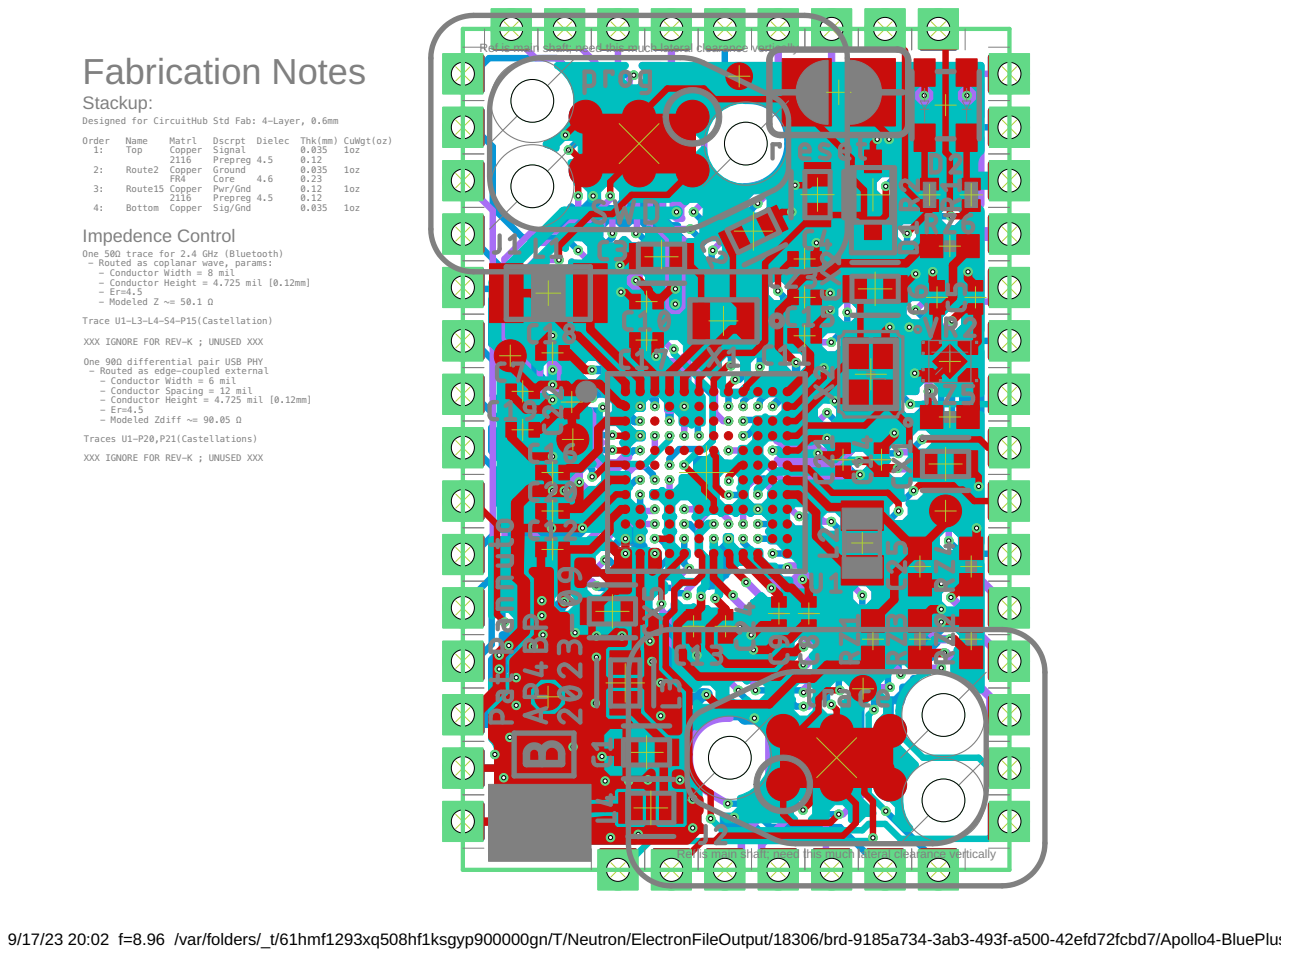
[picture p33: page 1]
Fabrication Notes; Order; Name; Matrl; Dscrpt Dielec Thk(mm) CuWgt(oz); Top; Copper Signal; Prepreg 4.5; Route2 Copper Ground; Core; Route15 Copper Pwr/Gnd; Bottom Copper Sig/Gnd; Stackup:; AGND/GND Connection

Ref is main shaft; need this much lateral clearance vertically

Designed for CircuitHub Std Fab: 4-Layer, 0.6mm
Impedence Control

One 50Ω trace for 2.4 GHz (Bluetooth)
- Routed as coplanar wave, params:
- Conductor Width = 8 mil
- Conductor Height = 4.725 mil [0.12mm]
- Modeled Z ~= 50.1 Ω
Trace U1-L3-L4-S4-P15(Castellation)

XXX IGNORE FOR REV-K ; UNUSED XXX
One 90Ω differential pair USB PHY
- Routed as edge-coupled external
- Conductor Width = 6 mil
- Conductor Spacing = 12 mil
- Modeled Zdiff ~= 90.05 Ω
Traces U1-P20,P21(Castellations)

9/17/23 20:02 f=8.96 /var/folders/_t/61hmf1293xq508hf1ksgyp900000gn/T/Neutron/ElectronFileOutput/18306/brd-9185a734-3ab3-493f-a500-42efd72fcbd7/Apollo4-BluePlus

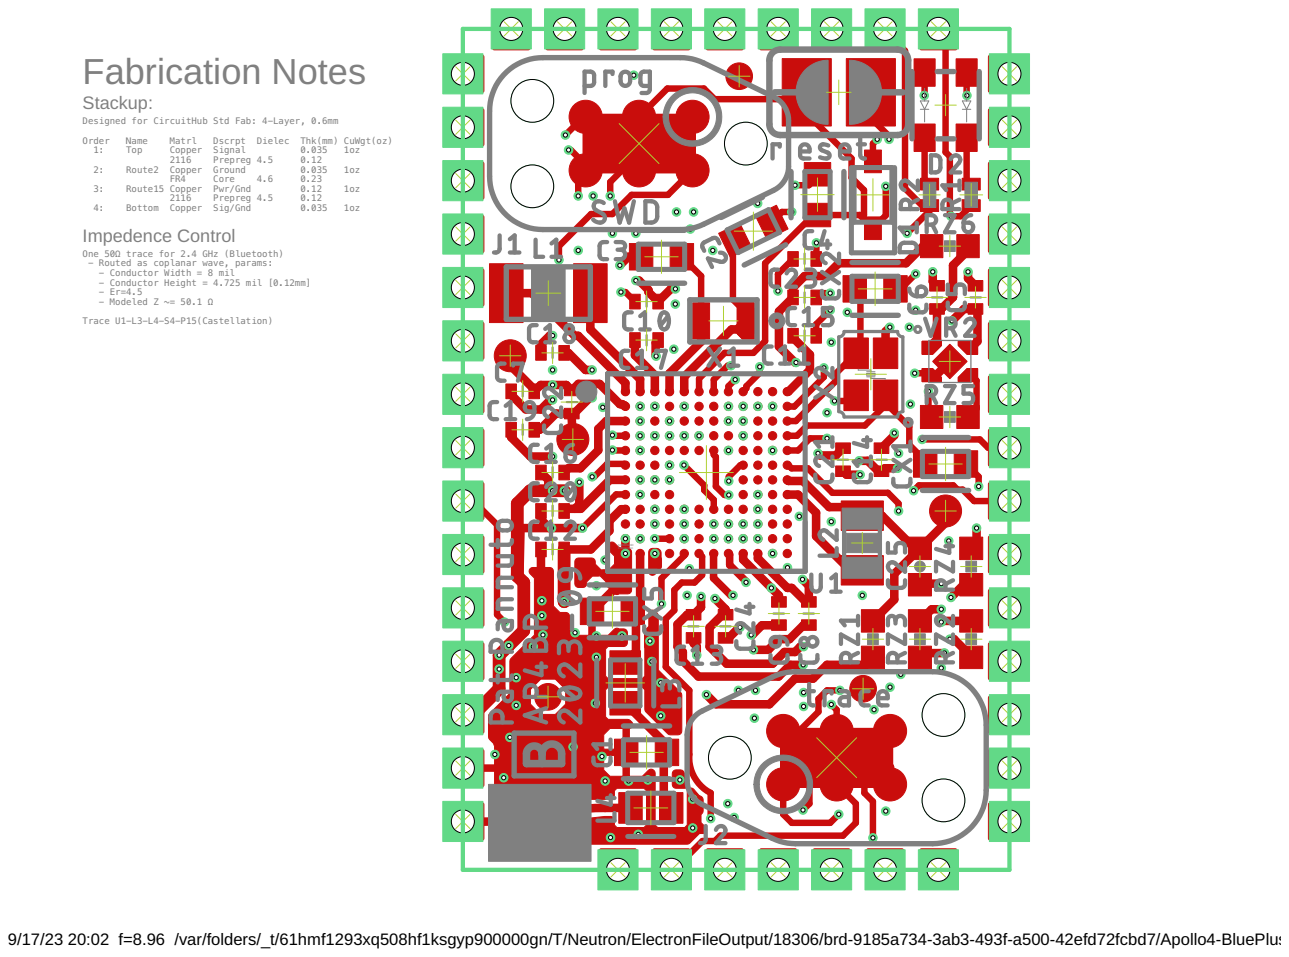
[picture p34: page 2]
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

Designed for CircuitHub Std Fab: 4-Layer, 0.6mm
Impedence Control

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

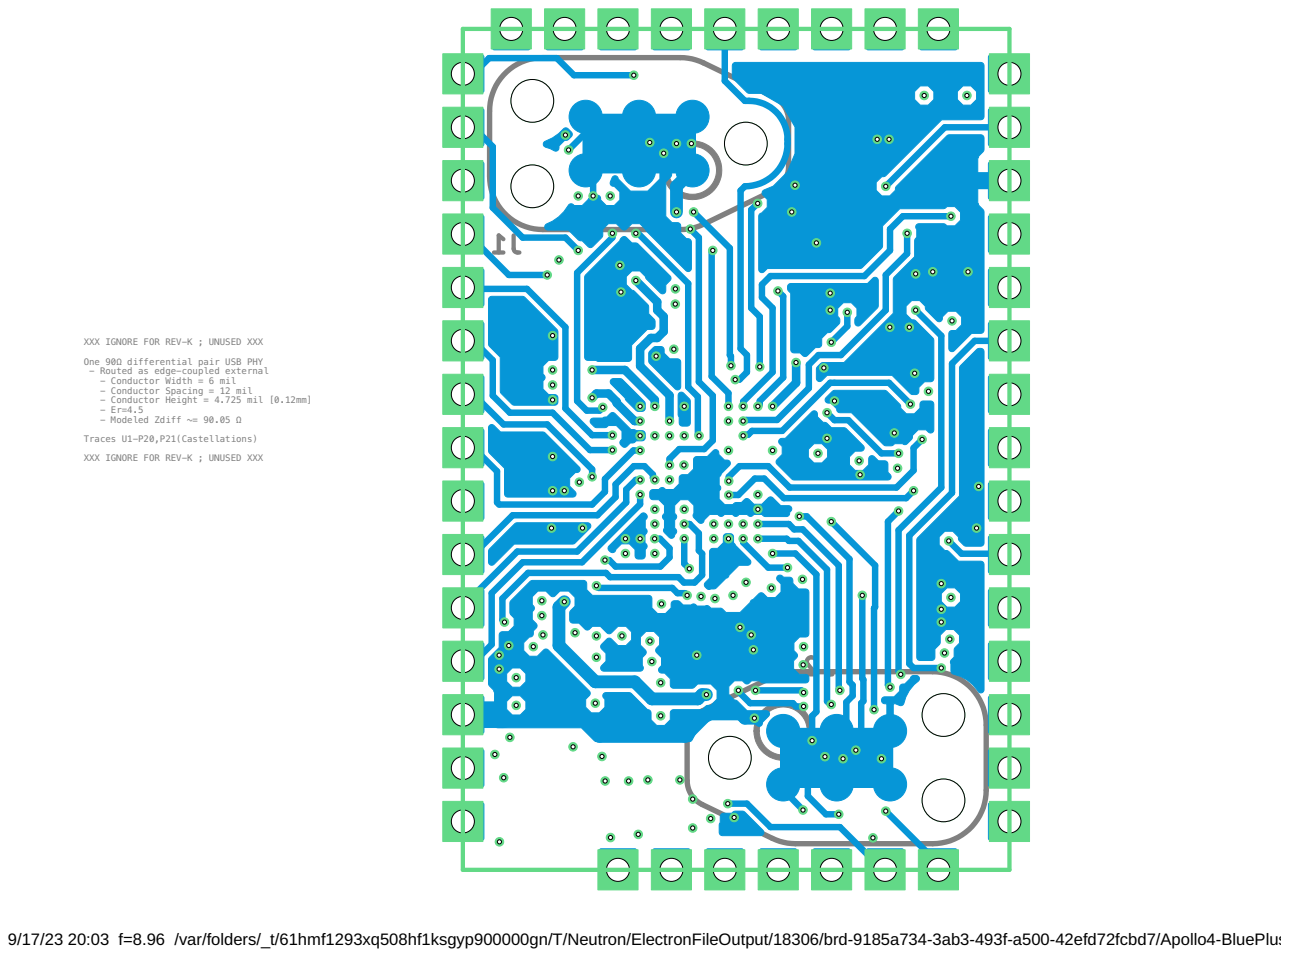
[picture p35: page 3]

XXX IGNORE FOR REV-K ; UNUSED XXX
One 90Ω differential pair USB PHY
- Routed as edge-coupled external
- Conductor Width = 6 mil
- Conductor Spacing = 12 mil
- Conductor Height = 4.725 mil [0.12mm]
- Modeled Zdiff ~= 90.05 Ω
Traces U1-P20,P21(Castellations)

9/17/23 20:03 f=8.96 /var/folders/_t/61hmf1293xq508hf1ksgyp900000gn/T/Neutron/ElectronFileOutput/18306/brd-9185a734-3ab3-493f-a500-42efd72fcbd7/Apollo4-BluePlus

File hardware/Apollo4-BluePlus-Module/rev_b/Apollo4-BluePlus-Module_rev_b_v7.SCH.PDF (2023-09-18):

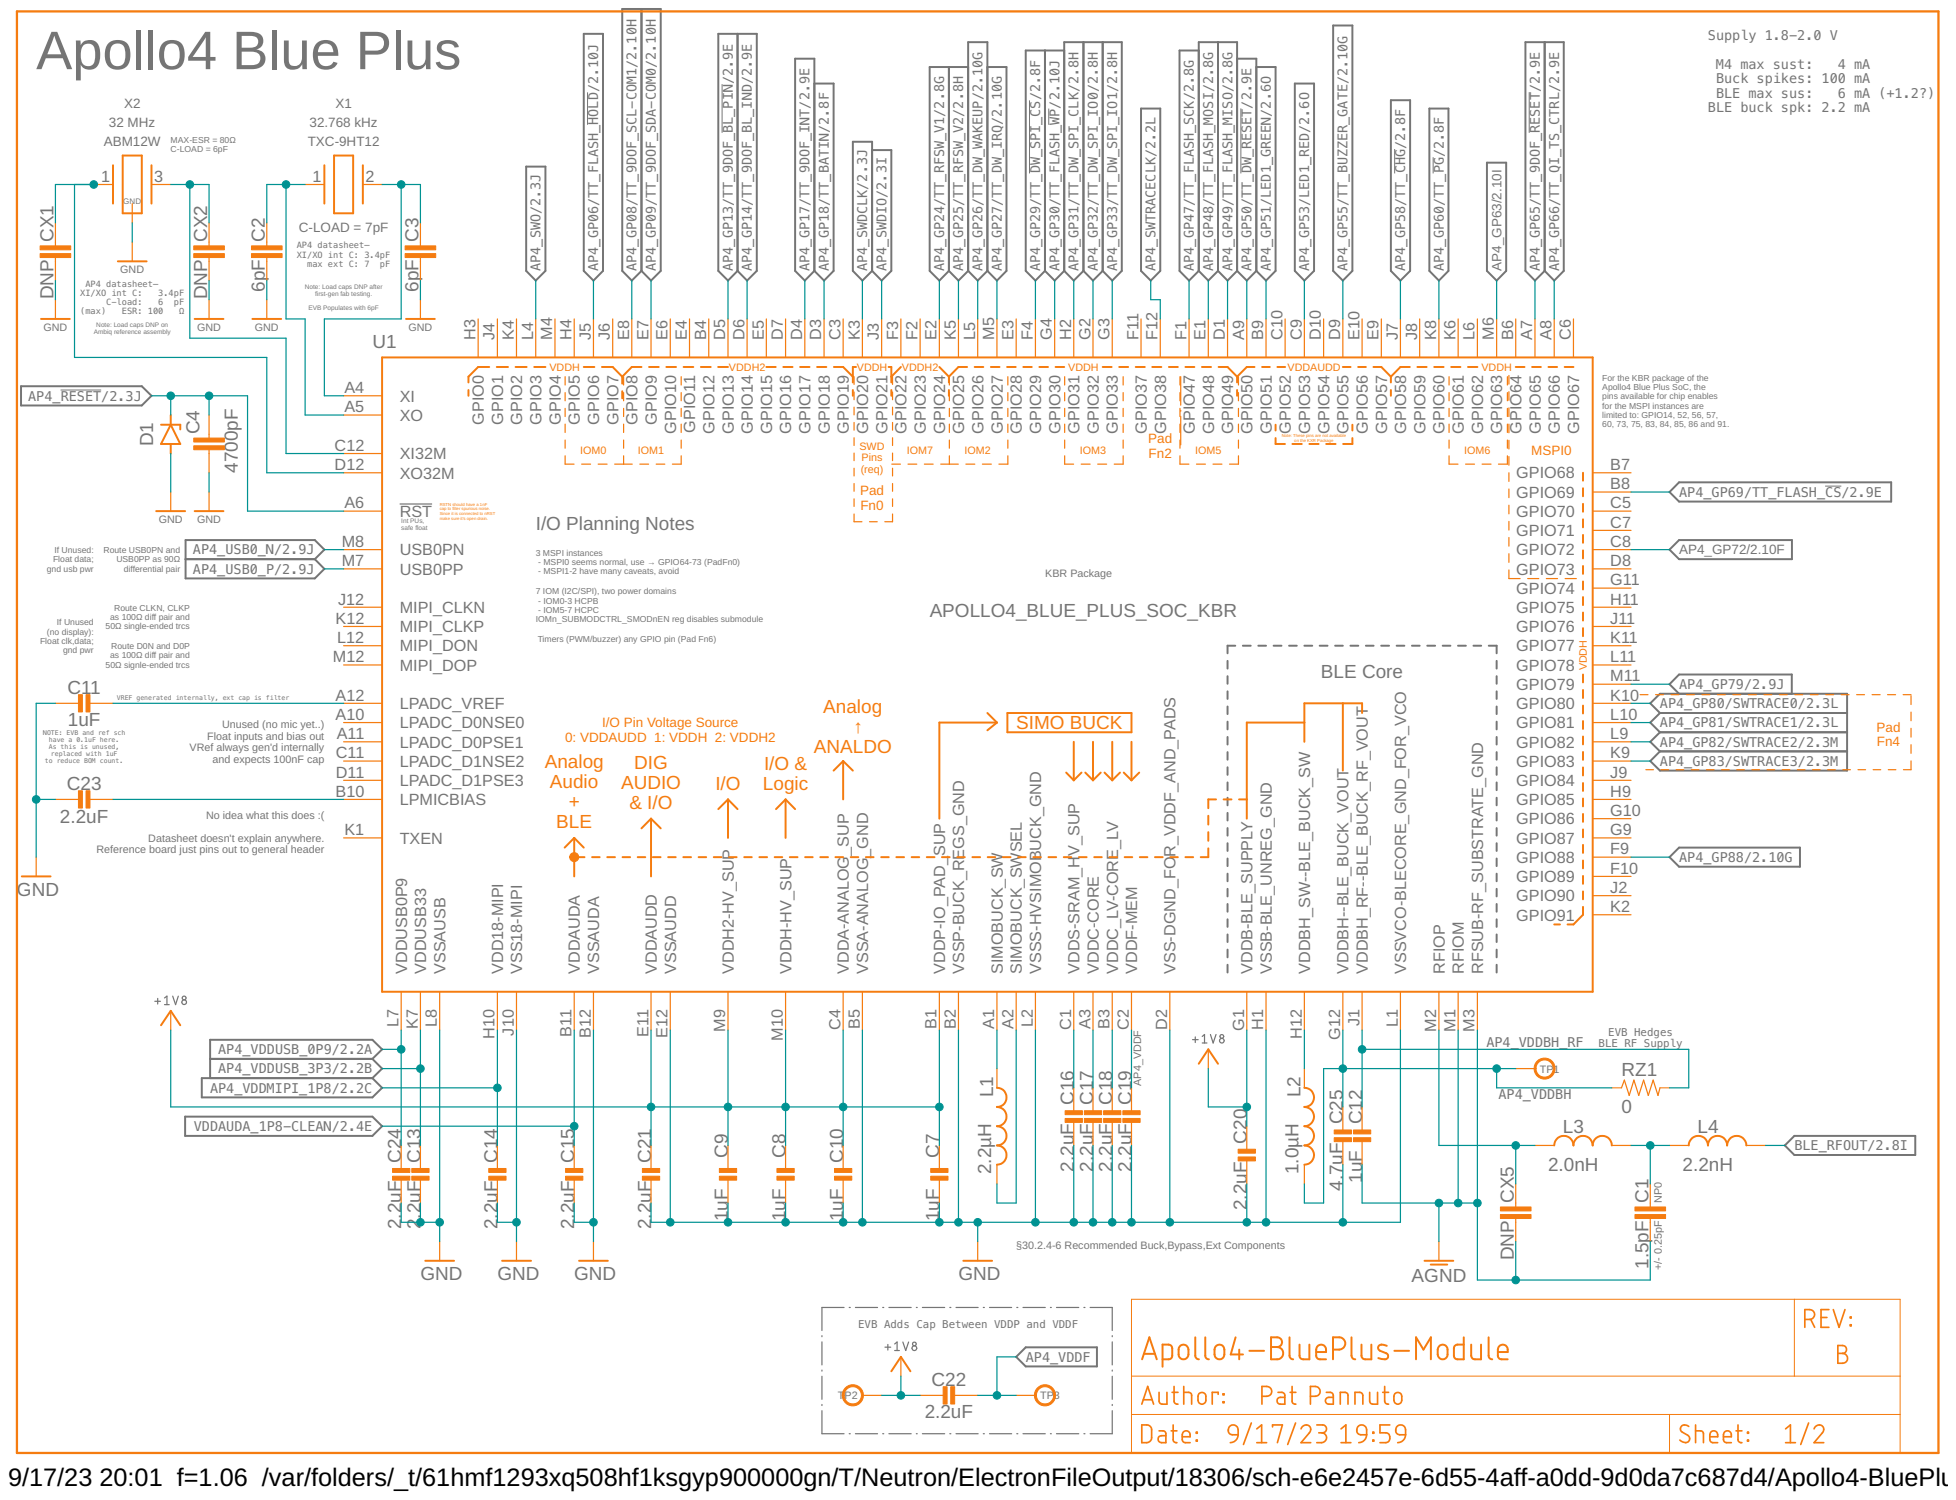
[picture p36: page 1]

Supply 1.8-2.0 V
Buck spikes: 100 mA
BLE buck spk: 2.2 mA

Note: Load caps DNP after
first-gen fab testing. EVB Populates with 6pF

Note: Load caps DNP on Ambiq reference assembly

For the KBR package of the Apollo4 Blue Plus SoC, the
pins available for chip enables
for the MSPI instances are
limited to: GPIO14, 52, 56, 57, 60, 73, 75, 83, 84, 85, 86 and 91.

Note: These pins are not available
on the KXR Package

RSTN should have a 1nF
cap to filter spurious noise. Since it is connected to nRST make sure it’s open drain.

Int PUs, safe float If Unused: Float data; gnd usb pwr

Route USB0PN and USB0PP as 90Ω
differential pair Route CLKN, CLKP

3 MSPI instances
- MSPI0 seems normal, use → GPIO64-73 (PadFn0)
- MSPI1-2 have many caveats, avoid

7 IOM (I2C/SPI), two power domains
- IOM0-3 HCPB
- IOM5-7 HCPC
IOMn_SUBMODCTRL_SMODnEN reg disables submodule Timers (PWM/buzzer) any GPIO pin (Pad Fn6)

as 100Ω diff pair and
50Ω single-ended trcs Route D0N and D0P

VREF generated internally, ext cap is filter

NOTE: EVB and ref sch
have a 0.1uF here.
As this is unused,
replaced with 1uF

§30.2.4-6 Recommended Buck,Bypass,Ext Components
GND

EVB Adds Cap Between VDDP and VDDF

9/17/23 20:01 f=1.06 /var/folders/_t/61hmf1293xq508hf1ksgyp900000gn/T/Neutron/ElectronFileOutput/18306/sch-e6e2457e-6d55-4aff-a0dd-9d0da7c687d4/Apollo4-BluePlus-Module_rev_b v6.sch (Sheet: 1/2)

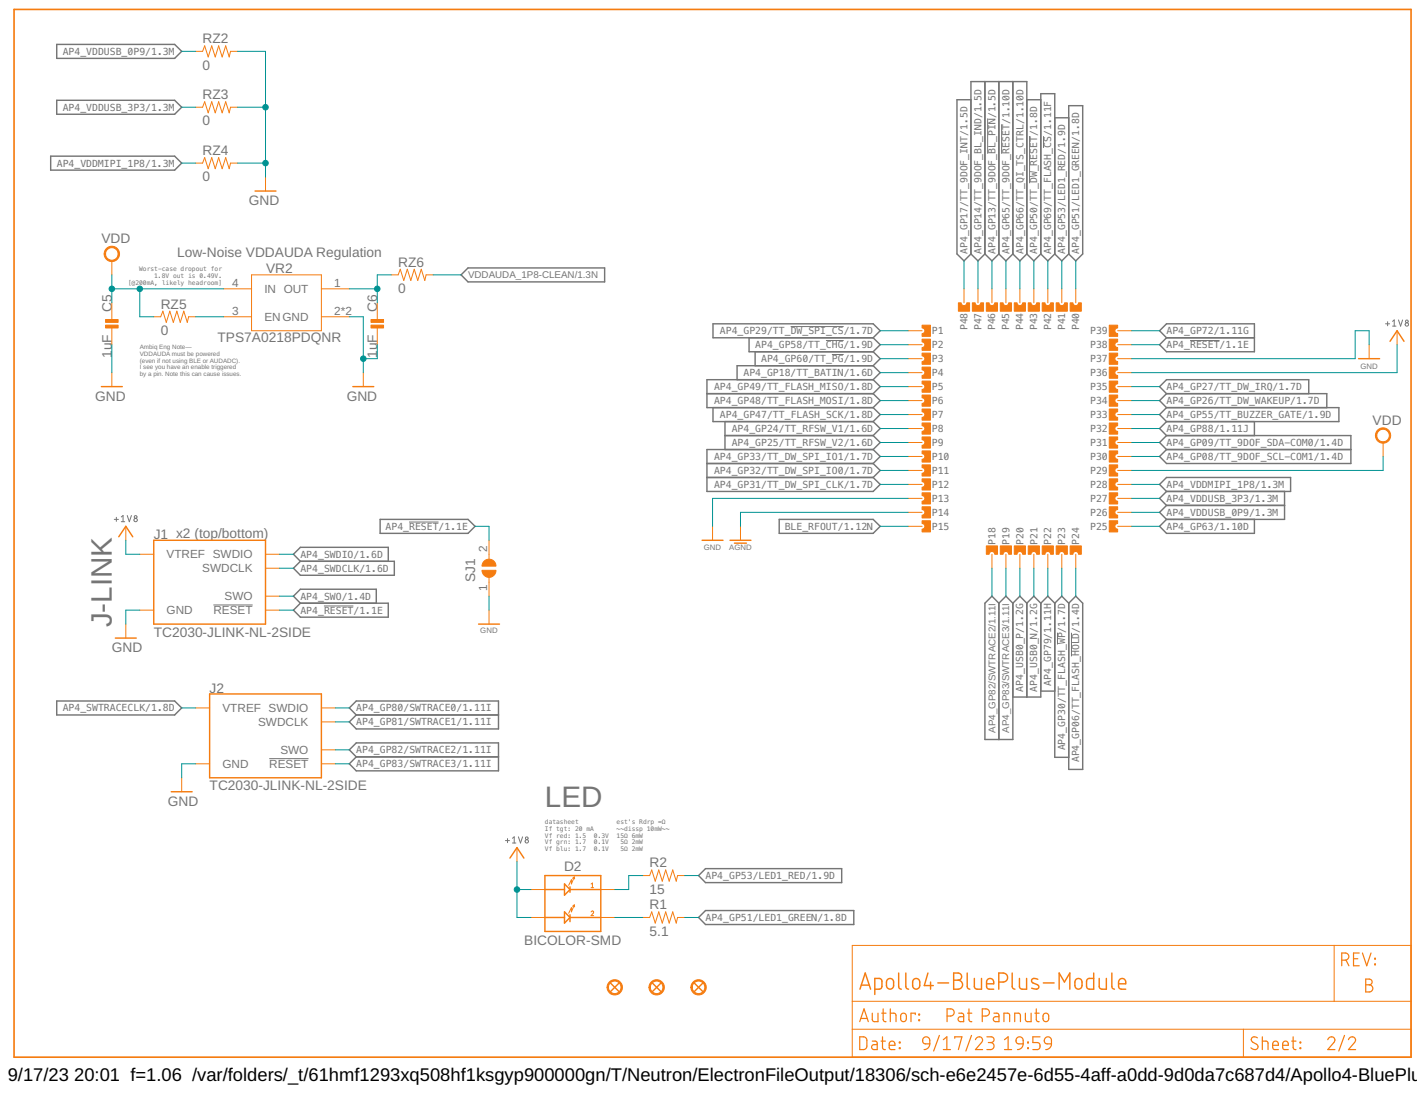
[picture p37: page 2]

Low-Noise VDDAUDA Regulation

Ambiq Eng Note—
VDDAUDA must be powered
(even if not using BLE or AUDADC).
I see you have an enable triggered
by a pin. Note this can cause issues.

9/17/23 20:01 f=1.06 /var/folders/_t/61hmf1293xq508hf1ksgyp900000gn/T/Neutron/ElectronFileOutput/18306/sch-e6e2457e-6d55-4aff-a0dd-9d0da7c687d4/Apollo4-BluePlus-Module_rev_b v6.sch (Sheet: 2/2)

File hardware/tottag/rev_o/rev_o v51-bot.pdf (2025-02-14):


2/14/25 12:52 f=2.50 /Users/ppannuto/code/lab11/totternary/hardware/tottag/rev_o/rev_o v51-bot.pdf

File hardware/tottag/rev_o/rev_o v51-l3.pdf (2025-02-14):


2/14/25 12:51 f=2.50 /Users/ppannuto/code/lab11/totternary/hardware/tottag/rev_o/rev_o v51-l3.pdf

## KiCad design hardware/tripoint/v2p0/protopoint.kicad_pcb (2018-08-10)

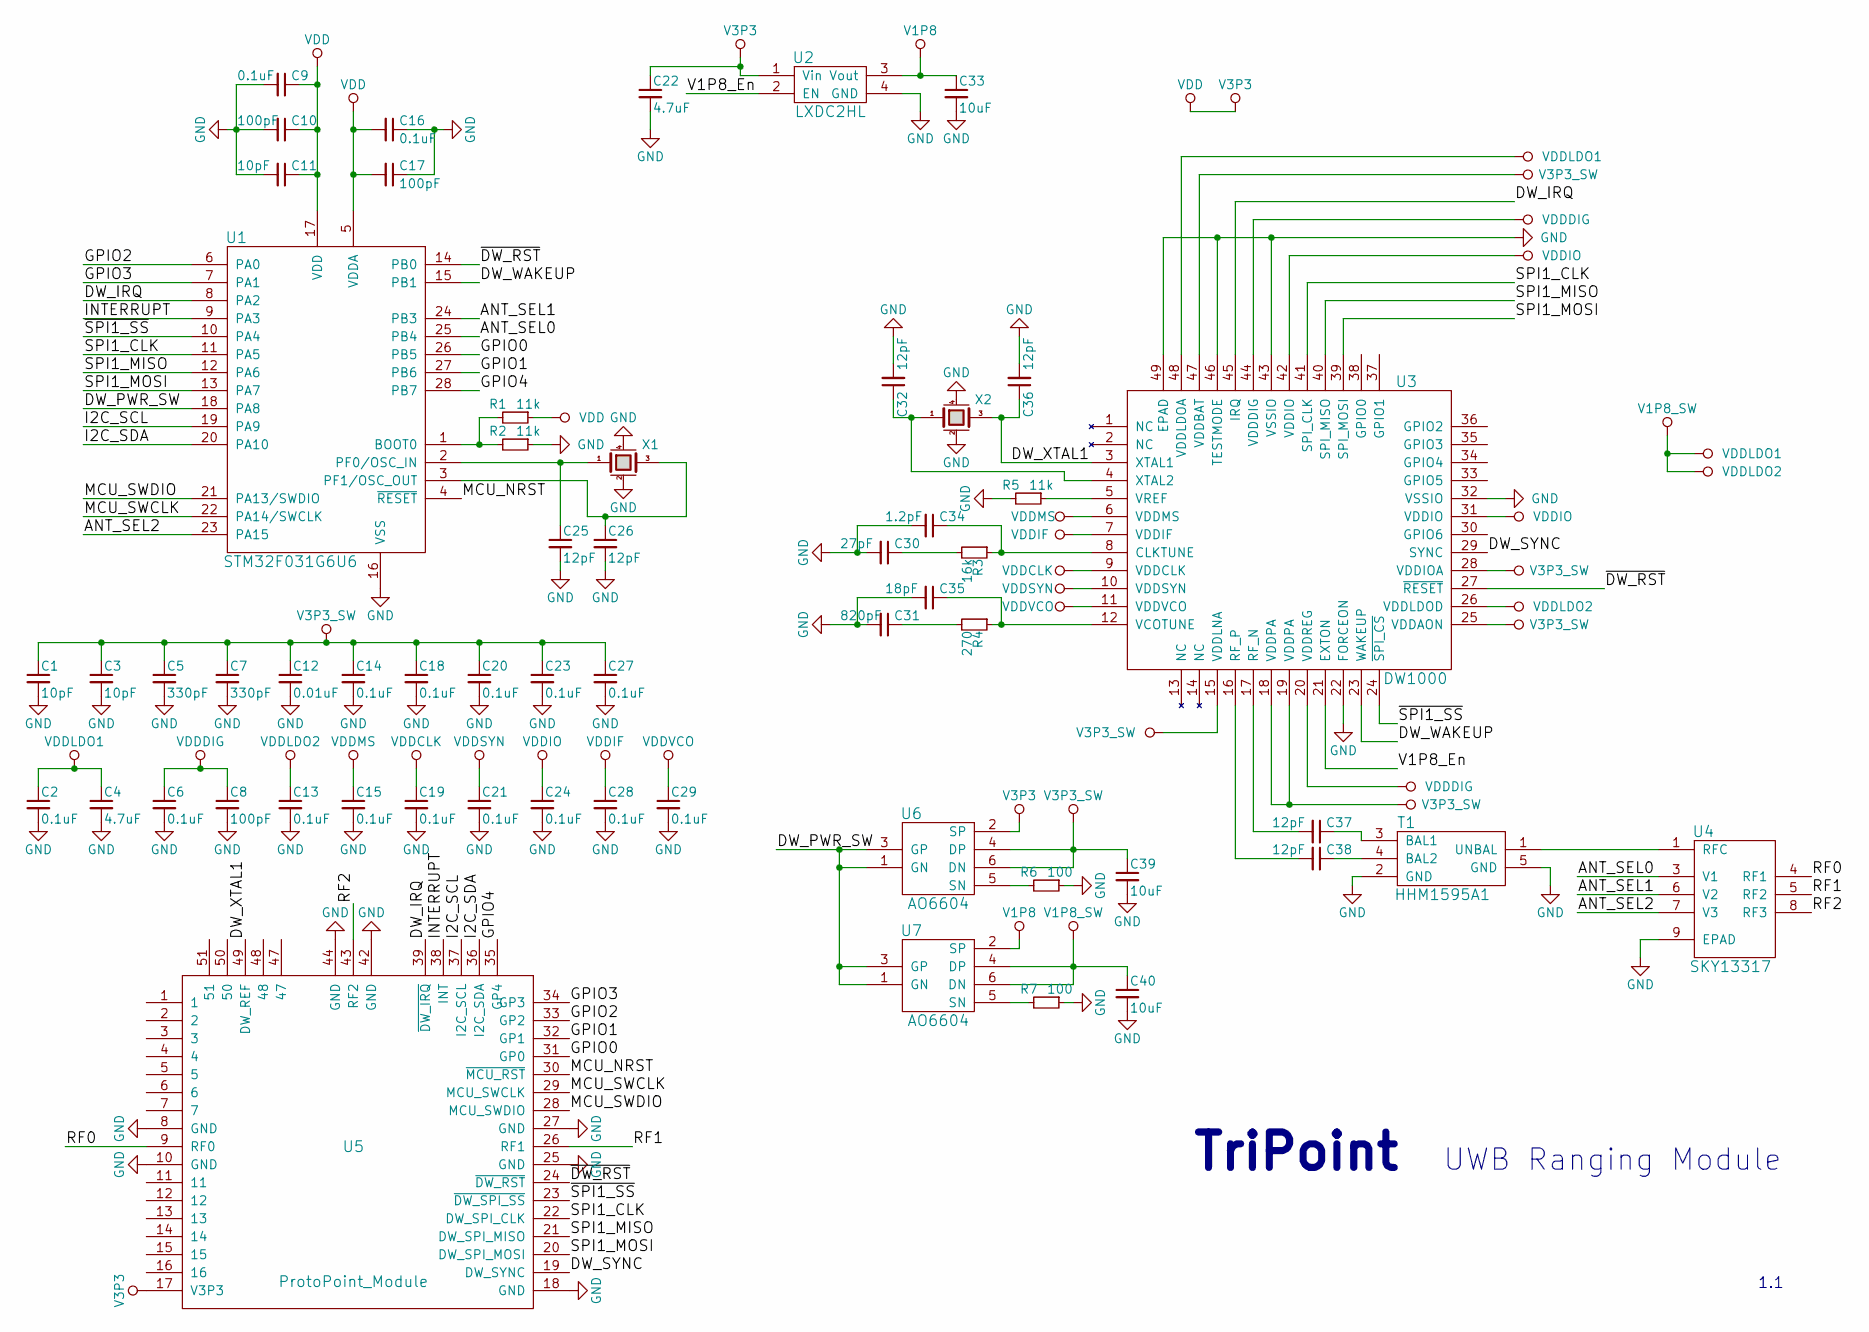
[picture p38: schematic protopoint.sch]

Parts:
C1, C3, C11: 10pF; C_0201; ManPartNo GRM0335C1E100JA01D
C2, C6, C9, C13, C14, C15, C16, C18, C19, C20, C21, C23, C24, C27, C28, C29: 0.1uF; C_0201; ManPartNo GRM033R61A104KE15D
C4, C22: 4.7uF; C_0603; ManPartNo GRM188F51A475ZE20D
C5, C7: 330pF; C_0201; ManPartNo GRM033R71E331KA01D
C8, C10, C17: 100pF; C_0201; ManPartNo GRM0335C1E101JA01D
C12: 0.01uF; C_0201; ManPartNo GRM033R71A103KA01D
C25, C26, C32, C36: 12pF; C_0201; ManPartNo GRM0335C1E120JA01D
C30: 27pF; C_0201; ManPartNo GRM0335C1E270JA01D
C31: 820pF; C_0201; ManPartNo GRM033R71E821KA01D
C33, C39, C40: 10uF; C_0603; ManPartNo GRM188R61C106MA73D
C34: 1.2pF; C_0201; ManPartNo GRM0335C1H1R2CA01D
C35: 18pF; C_0201; ManPartNo GRM0335C1H180JA01D
C37, C38: 12pF; C_0402; ManPartNo GRM1555C1H120JA01D
R1, R2, R5: 11k; R_0201; ManPartNo ERJ-1GEF1102C
R3: 16k; R_0201; ManPartNo ERJ-1GEF1602C
R4: 270; R_0201; ManPartNo ERJ-1GEF2700C
R6, R7: 100; R_0201; ManPartNo ERJ-1GEF1102C
T1: HHM1595A1; ManPartNo HHM1595A1
U1: STM32F031G6U6; UFQFPN-28; ManPartNo STM32F031G6U6
U2: LXDC2HL; ManPartNo LXDC2HL18A-052
U3: DW1000; QFN-48-EP-6x6mm; ManPartNo DW1000-I-TR13
U4: SKY13317; MLPQ-UT-8-1.5X1.5mm; ManPartNo SKY13317-373LF
U5: ProtoPoint_Module; ProtoPoint_Module_Castellated
U6, U7: AO6604; TSOP-6
X1: 38.4M; FA-128; ManPartNo FA-20H 38.4000MF10Z-AS3
X2: 16M; FA-128; ManPartNo FA-20H 16.0000MF10Z-AJ3

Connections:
/ANT_SEL0: U1.25 (PB4), U4.3 (V1)
/ANT_SEL1: U1.24 (PB3), U4.6 (V2)
/ANT_SEL2: U1.23 (PA15), U4.7 (V3)
/DW_IRQ: U1.8 (PA2), U3.45 (IRQ), U5.39 (~DW_IRQ)
/DW_PWR_SW: U1.18 (PA8), U6.1 (GN), U6.3 (GP), U7.1 (GN), U7.3 (GP)
/DW_SYNC: U3.29 (SYNC), U5.19 (DW_SYNC)
/DW_WAKEUP: U1.15 (PB1), U3.23 (WAKEUP)
/DW_XTAL1: C36.1, U3.3 (XTAL1), U5.49 (DW_REF), X2.3
/GPIO0: U1.26 (PB5), U5.31 (GP0)
/GPIO1: U1.27 (PB6), U5.32 (GP1)
/GPIO2: U1.6 (PA0), U5.33 (GP2)
/GPIO3: U1.7 (PA1), U5.34 (GP3)
/GPIO4: U1.28 (PB7), U5.35 (GP4)
/I2C_SCL: U1.19 (PA9), U5.37 (I2C_SCL)
/I2C_SDA: U1.20 (PA10), U5.36 (I2C_SDA)
/INTERRUPT: U1.9 (PA3), U5.38 (INT)
/MCU_NRST: U1.4 (~RESET), U5.30 (~MCU_RST)
/MCU_SWCLK: U1.22 (PA14/SWCLK), U5.29 (MCU_SWCLK)
/MCU_SWDIO: U1.21 (PA13/SWDIO), U5.28 (MCU_SWDIO)
/RF0: U4.4 (RF1), U5.9 (RF0)
/RF1: U4.5 (RF2), U5.26 (RF1)
/RF2: U4.8 (RF3), U5.43 (RF2)
/SPI1_CLK: U1.11 (PA5), U3.41 (SPI_CLK), U5.22 (DW_SPI_CLK)
/SPI1_MISO: U1.12 (PA6), U3.40 (SPI_MISO), U5.21 (DW_SPI_MISO)
/SPI1_MOSI: U1.13 (PA7), U3.39 (SPI_MOSI), U5.20 (DW_SPI_MOSI)
/V1P8_En: U2.2 (EN), U3.21 (EXTON)
/~DW_RST: U1.14 (PB0), U3.27 (~RESET), U5.24 (~DW_RST)
/~SPI1_SS: U1.10 (PA4), U3.24 (~SPI_CS), U5.23 (~DW_SPI_SS)
GND: C1.2, C2.2, C3.2, C4.2, C5.2, C6.2, C7.2, C8.2, C9.2, C10.2, C11.2, C12.2, C13.2, C14.2, C15.2, C16.1, C17.1, C18.2, C19.2, C20.2, C21.2, C22.2, C23.2, C24.2, C25.2, C26.2, C27.2, C28.2, C29.2, C30.2, C31.2, C32.2, C33.2, C34.2, C35.2, C36.2, C39.2, C40.2, R2.1, R5.2, R6.1, R7.1, T1.2 (GND), T1.5 (GND), U1.16 (VSS), U2.4 (GND), U3.22 (FORCEON), U3.32 (VSSIO), U3.43 (VSSIO), U3.46 (TESTMODE), U3.49 (EPAD), U4.9 (EPAD), U5.8 (GND), U5.10 (GND), U5.18 (GND), U5.25 (GND), U5.27 (GND), U5.42 (GND), U5.44 (GND), X1.2 (case), X1.4, X2.2 (case), X2.4
unnamed: C25.1, U1.2 (PF0/OSC_IN), X1.1
unnamed: C26.1, U1.3 (PF1/OSC_OUT), X1.3
unnamed: C30.1, R3.2
unnamed: C31.1, R4.2
unnamed: C32.1, U3.4 (XTAL2), X2.1
unnamed: C34.1, R3.1, U3.8 (CLKTUNE)
unnamed: C35.1, R4.1, U3.12 (VCOTUNE)
unnamed: C37.1, T1.3 (BAL1)
unnamed: C37.2, U3.17 (RF_N)
unnamed: C38.1, T1.4 (BAL2)
unnamed: C38.2, U3.16 (RF_P)
unnamed: R1.2, R2.2, U1.1 (BOOT0)
unnamed: R5.1, U3.5 (VREF)
unnamed: R6.2, U6.5 (SN)
unnamed: R7.2, U7.5 (SN)
unnamed: T1.1 (UNBAL), U4.1 (RFC)
V1P8: C33.1, U2.3 (Vout), U7.2 (SP)
V1P8_SW: C2.1, C4.1, C13.1, C40.1, U3.26 (VDDLDOD), U3.48 (VDDLDOA), U7.4 (DP), U7.6 (DN)
V3P3: C9.1, C10.1, C11.1, C16.2, C17.2, C22.1, R1.1, U1.5 (VDDA), U1.17 (VDD), U2.1 (Vin), U5.17 (V3P3), U6.2 (SP)
V3P3_SW: C1.1, C3.1, C5.1, C7.1, C12.1, C14.1, C18.1, C20.1, C23.1, C27.1, C39.1, U3.15 (VDDLNA), U3.18 (VDDPA), U3.19 (VDDPA), U3.25 (VDDAON), U3.28 (VDDIOA), U3.47 (VDDBAT), U6.4 (DP), U6.6 (DN)
VDDCLK: C19.1, U3.9 (VDDCLK)
VDDDIG: C6.1, C8.1, U3.20 (VDDREG), U3.44 (VDDDIG)
VDDIF: C28.1, U3.7 (VDDIF)
VDDIO: C24.1, U3.31 (VDDIO), U3.42 (VDDIO)
VDDMS: C15.1, U3.6 (VDDMS)
VDDSYN: C21.1, U3.10 (VDDSYN)
VDDVCO: C29.1, U3.11 (VDDVCO)

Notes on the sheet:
TriPoint
1.1
UWB Ranging Module

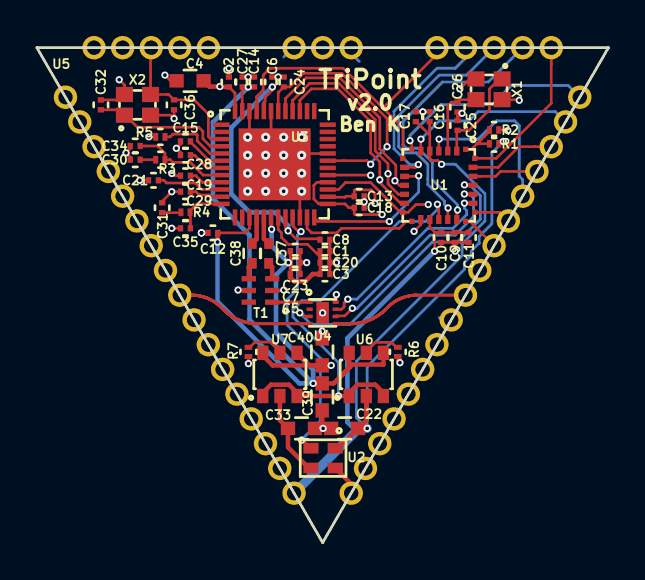
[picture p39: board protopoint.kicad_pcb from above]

Board: 4 copper layers, 31.8 x 27.5 mm, 57 parts (0 on the bottom side), 56 nets.

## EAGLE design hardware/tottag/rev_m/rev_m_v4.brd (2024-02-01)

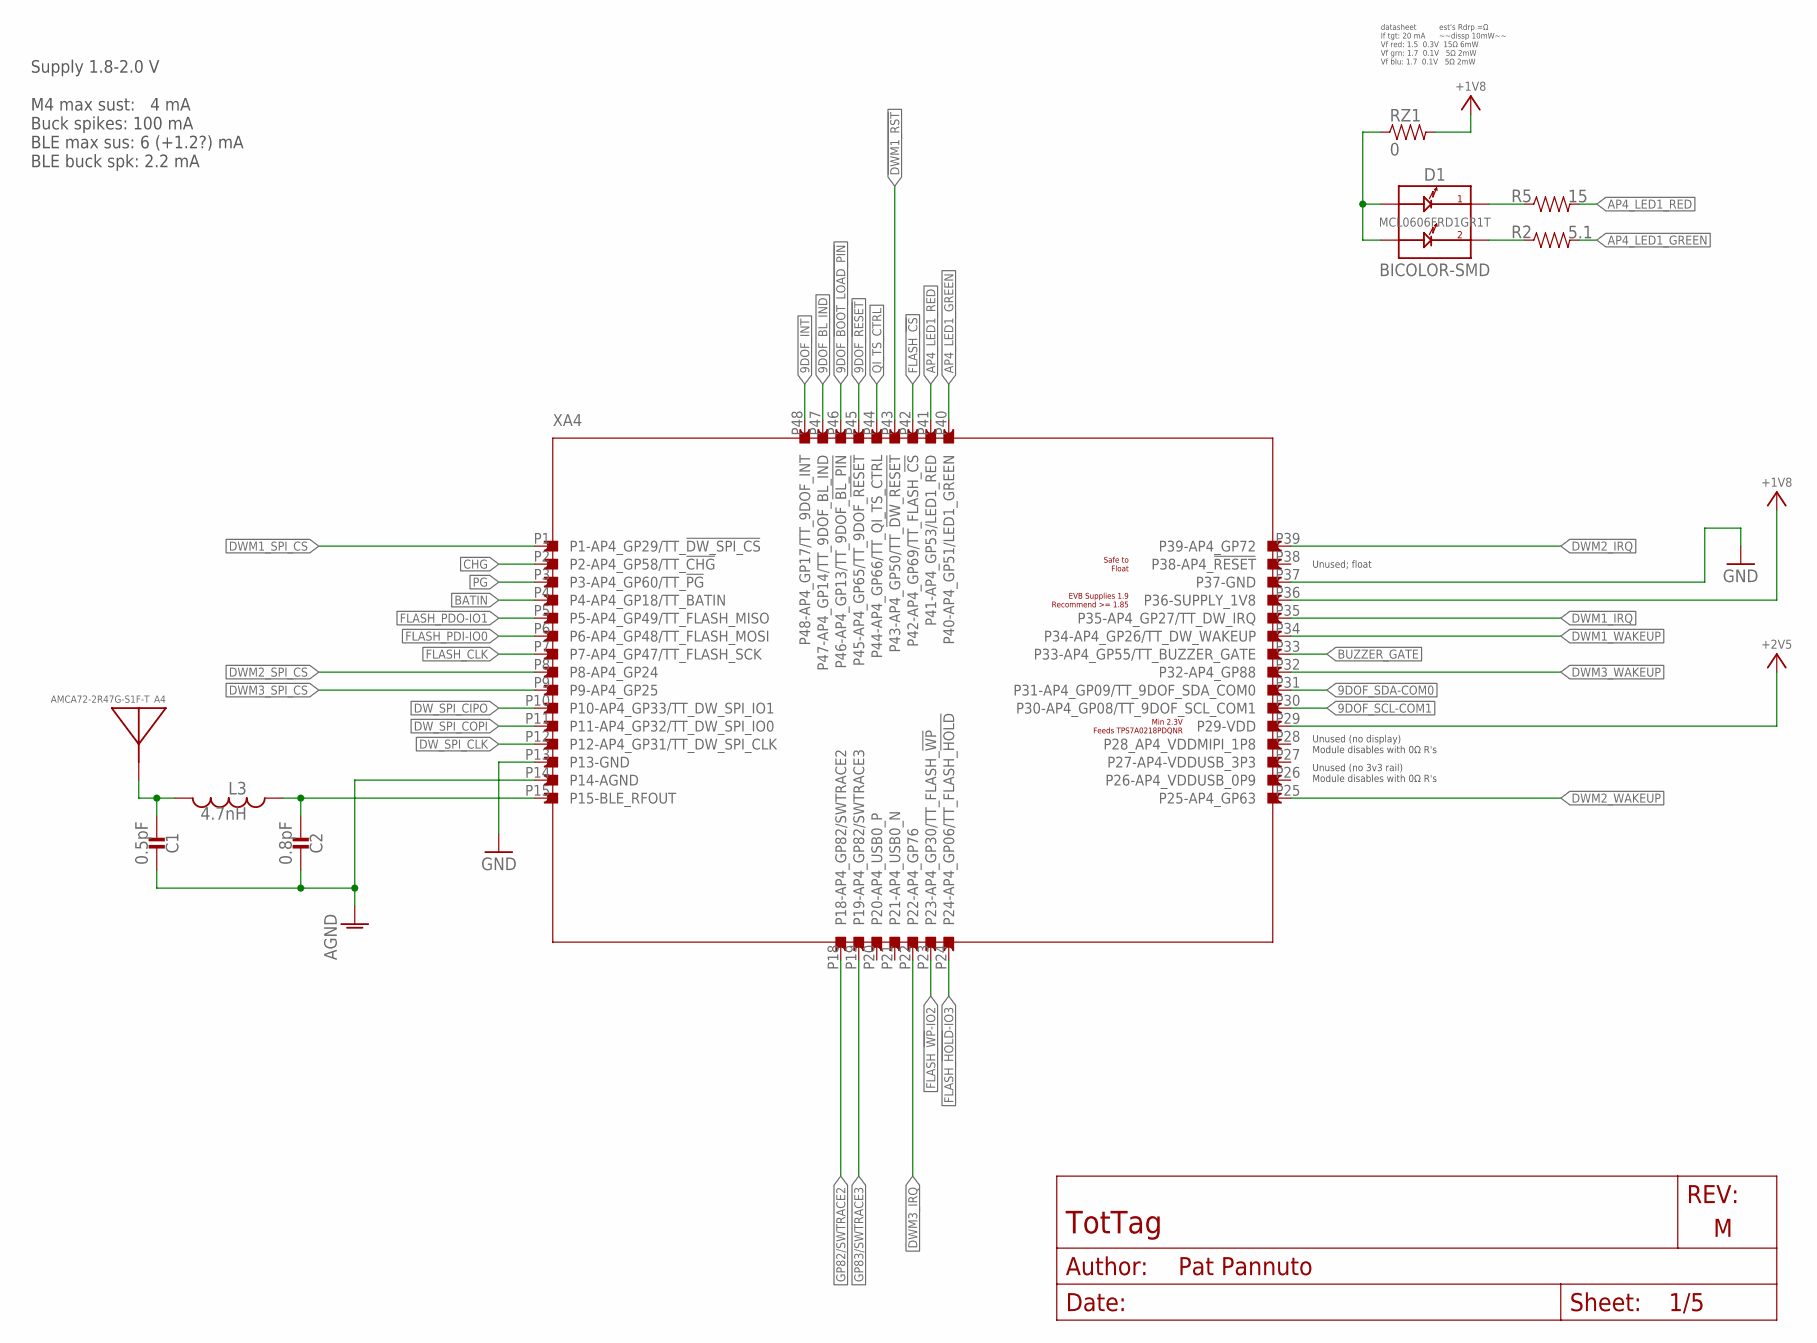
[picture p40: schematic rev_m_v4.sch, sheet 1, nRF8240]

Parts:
A4: AMCA72-2R47G-S1F-T; AMCA72-2R470G-S1F-T
C1: 0.5pF; 0402_CAP; MPN GJM1555C1HR50WB01D
C2: 0.8pF; 0402_CAP; MPN GJM1555C1HR80WB01D
D1: BICOLOR-SMD; LED-0606; MPN MCL0606FRD1GR1T
L3: 4.7nH; 0402_CAP; MPN LQW15AN4N7G8ZD
R2: 5.1; 0402_RES; MPN RC0402JR-075R1L
R5: 15; 0402_RES; MPN RC0402JR-0715RL
RZ1: 0; 0603-RES; MPN RMCF0603ZT0R00
XA4: APOLLO4_BLUEPLUS_MODULE

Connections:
9DOF_!BOOT_LOAD_PIN: XA4.P46 (P46-AP4_GP13/TT_9DOF_!BL_PIN); also elsewhere on the board
9DOF_!RESET: XA4.P45 (P45-AP4_GP65/TT_9DOF_!RESET); also elsewhere on the board
9DOF_BL_IND: XA4.P47 (P47-AP4_GP14/TT_9DOF_BL_IND); also elsewhere on the board
9DOF_INT: XA4.P48 (P48-AP4_GP17/TT_9DOF_INT); also elsewhere on the board
9DOF_SCL-COM1: XA4.P30 (P30-AP4_GP08/TT_9DOF_SCL_COM1); also elsewhere on the board
9DOF_SDA-COM0: XA4.P31 (P31-AP4_GP09/TT_9DOF_SDA_COM0); also elsewhere on the board
!CHG: XA4.P2 (P2-AP4_GP58/TT_!CHG); also elsewhere on the board
!DWM1_RST: XA4.P43 (P43-AP4_GP50/TT_!DW_RESET); also elsewhere on the board
!DWM1_SPI_CS: XA4.P1 (P1-AP4_GP29/TT_!DW_SPI_CS); also elsewhere on the board
!DWM2_SPI_CS: XA4.P8 (P8-AP4_GP24); also elsewhere on the board
!DWM3_SPI_CS: XA4.P9 (P9-AP4_GP25); also elsewhere on the board
!PG: XA4.P3 (P3-AP4_GP60/TT_!PG); also elsewhere on the board
+1V8: RZ1.2, XA4.P36 (P36-SUPPLY_1V8); also elsewhere on the board
+2V5: XA4.P29 (P29-VDD); also elsewhere on the board
AGND: C1.2, C2.2, XA4.P14 (P14-AGND)
AP4_LED1_GREEN: R2.2, XA4.P40 (P40-AP4_GP51/LED1_GREEN)
AP4_LED1_RED: R5.2, XA4.P41 (P41-AP4_GP53/LED1_RED)
AP4_LED2_BLUE_COMM: D1.C1, R5.1
AP4_LED_RED_COMM: D1.C2, R2.1
AP4_RFIOP: C2.1, L3.2, XA4.P15 (P15-BLE_RFOUT)
BATIN: XA4.P4 (P4-AP4_GP18/TT_BATIN); also elsewhere on the board
BLE_ANT_FEED: A4.S1, C1.1, L3.1
BUZZER_GATE: XA4.P33 (P33-AP4_GP55/TT_BUZZER_GATE); also elsewhere on the board
DWM1_IRQ: XA4.P35 (P35-AP4_GP27/TT_DW_IRQ); also elsewhere on the board
DWM1_WAKEUP: XA4.P34 (P34-AP4_GP26/TT_DW_WAKEUP); also elsewhere on the board
DWM2_IRQ: XA4.P39 (P39-AP4_GP72); also elsewhere on the board
DWM2_WAKEUP: XA4.P25 (P25-AP4_GP63); also elsewhere on the board
DWM3_IRQ: XA4.P22 (P22-AP4_GP76); also elsewhere on the board
DWM3_WAKEUP: XA4.P32 (P32-AP4_GP88); also elsewhere on the board
DW_SPI_CIPO: XA4.P10 (P10-AP4_GP33/TT_DW_SPI_IO1); also elsewhere on the board
DW_SPI_CLK: XA4.P12 (P12-AP4_GP31/TT_DW_SPI_CLK); also elsewhere on the board
DW_SPI_COPI: XA4.P11 (P11-AP4_GP32/TT_DW_SPI_IO0); also elsewhere on the board
FLASH_!CS: XA4.P42 (P42-AP4_GP69/TT_FLASH_!CS); also elsewhere on the board
FLASH_!HOLD!-IO3: XA4.P24 (P24-AP4_GP06/TT_FLASH_!HOLD); also elsewhere on the board
FLASH_!WP!-IO2: XA4.P23 (P23-AP4_GP30/TT_FLASH_!WP); also elsewhere on the board
FLASH_CLK: XA4.P7 (P7-AP4_GP47/TT_FLASH_SCK); also elsewhere on the board
FLASH_PDI-IO0: XA4.P6 (P6-AP4_GP48/TT_FLASH_MOSI); also elsewhere on the board
FLASH_PDO-IO1: XA4.P5 (P5-AP4_GP49/TT_FLASH_MISO); also elsewhere on the board
GND: XA4.P13 (P13-GND), XA4.P37 (P37-GND); also elsewhere on the board
GP82/SWTRACE2: XA4.P18 (P18-AP4_GP82/SWTRACE2); also elsewhere on the board
GP83/SWTRACE3: XA4.P19 (P19-AP4_GP82/SWTRACE3); also elsewhere on the board
LED_SUP: D1.A1, D1.A2, RZ1.1
QI_TS_CTRL: XA4.P44 (P44-AP4_GP66/TT_QI_TS_CTRL); also elsewhere on the board

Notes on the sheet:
Supply 1.8-2.0 V M4 max sust: 4 mA Buck spikes: 100 mA BLE max sus: 6 (+1.2?) mA BLE buck spk: 2.2 mA
Unused (no 3v3 rail) Module disables with 0Ω R's
Unused (no display) Module disables with 0Ω R's
datasheet est's Rdrp =Ω If tgt: 20 mA ~~dissp 10mW~~ Vf red: 1.5 0.3V 15Ω 6mW Vf grn: 1.7 0.1V 5Ω 2mW Vf blu: 1.7 0.1V 5Ω 2mW
Unused; float

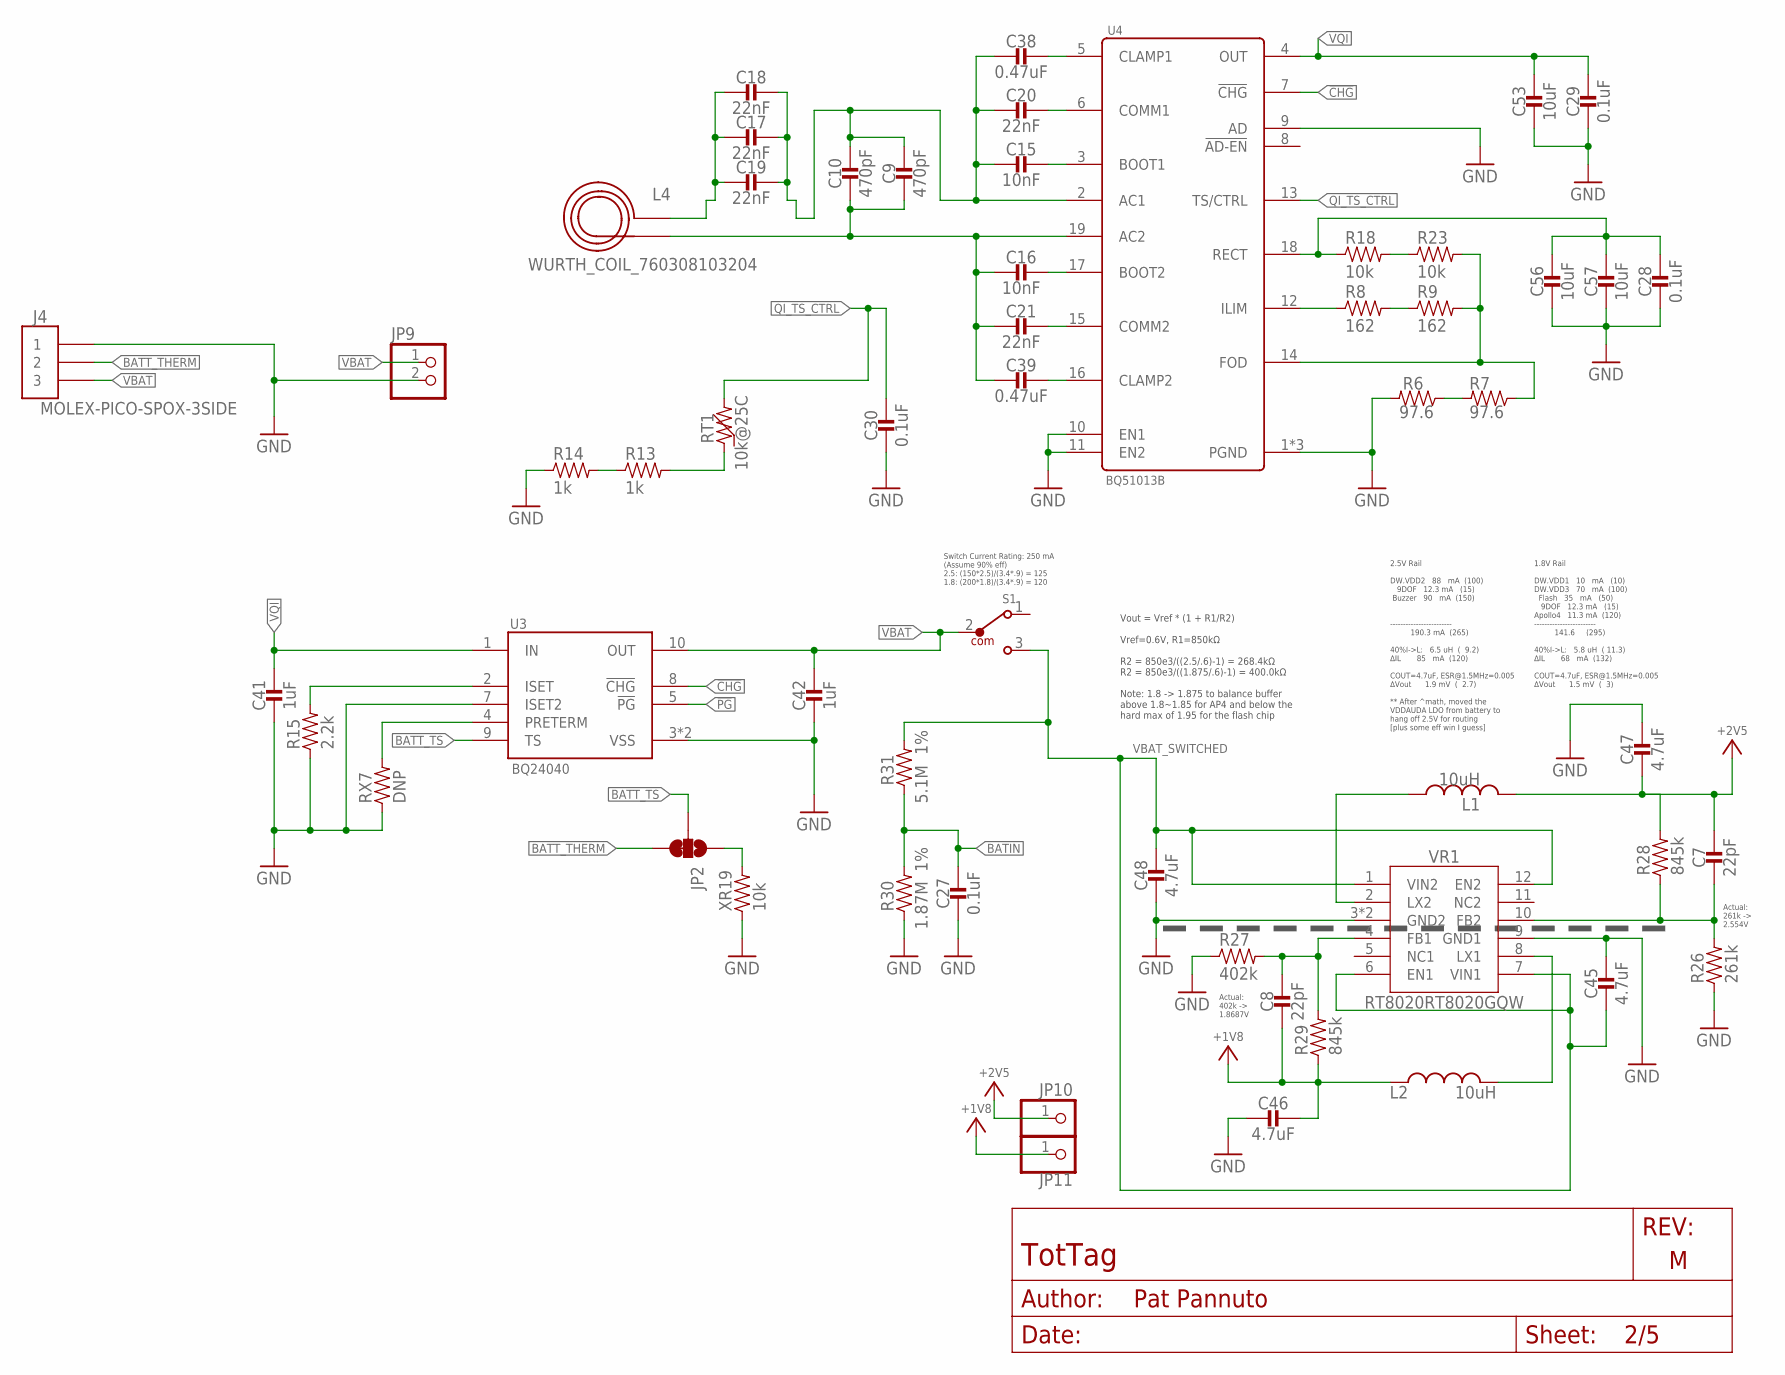
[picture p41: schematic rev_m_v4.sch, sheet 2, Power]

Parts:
C7, C8: 22pF; 0201_CAP; MPN GRM0335C1H220FA01D
C9, C10: 470pF; 0402_CAP; MPN GRM1555C1H471JA01J; DIGIKEY 490-6242-1-ND
C15, C16: 10nF; 0402_CAP; MPN GRM155R71H103KA88J; DIGIKEY 490-6351-2-ND
C17, C18, C19: 22nF; 0402_CAP; MPN GRM155R71E223JA61D; DIGIKEY 490-10699-2-ND
C20, C21: 22nF; 0402_CAP; MPN CC0402ZRY5V8BB223; DIGIKEY 311-3823-1-ND
C27, C28, C29, C30: 0.1uF; 0402_CAP; MPN GRM155R71C104KA88J; DIGIKEY 490-6328-1-ND
C38, C39: 0.47uF; 0402_CAP; MPN GRT155R61E474ME01D; DIGIKEY 490-12270-1-ND
C41, C42: 1uF; 0402_CAP; MPN GRM155R70J105KA12J
C45, C46, C47, C48: 4.7uF; 0603_CAP; MPN C1608X7S1A475K080AC
C53, C56, C57: 10uF; 0603_CAP; MPN CM105X5R106M25AT; DIGIKEY 1253-CM105X5R106M25ATCT-ND
J4: MOLEX-PICO-SPOX-3SIDE; MOLEX-PICO-SPOX-3_SIDE
JP2: JUMPER-SMT_3_1-NC_TRACE_SILK; SMT-JUMPER_3_1-NC_TRACE_SILK
JP9: PINHD-1X2; 1X02
JP10, JP11: PINHD-1X1; 1X01
L1, L2: 10uH; NRX3015; MPN NR3015T100M
L4: WURTH_COIL_760308103204
R6, R7: 97.6; 0402_RES; MPN RMCF0402FT97R6; DIGIKEY RMCF0402FT97R6CT-ND
R8, R9: 162; 0402_RES; MPN RMCF0402FT162R; DIGIKEY RMCF0402FT162RCT-ND
R13, R14: 1k; 0402_RES
R15: 2.2k; 0402_RES; MPN RMCF0402JT2K20; DIGIKEY RMCF0402JT2K20CT-ND
R18, R23: 10k; 0402_RES; MPN RC0402JR-0710KL; DIGIKEY 311-10KJRCT-ND
R26: 261k; 0201_RES; MPN ERJ-1GNF2613C
R27: 402k; 0201_RES; MPN ERJ-1GNF4023C
R28, R29: 845k; 0201_RES; MPN ERJ-1GNF8453C
R30: 1.87M; 0402_RES; TOLERANCE 1%; MPN RMCF0402FT1M87
R31: 5.1M; 0402_RES; TOLERANCE 1%; MPN RMCF0402FT5M10; DIGIKEY RMCF0402FT5M10CT-ND
RT1: 10k@25C; 0402_RES; MPN NCU15XH103F60RC; DIGIKEY 490-18149-1-ND
RX7: DNP; 0402_RES
S1: 450404015514; DIGIKEY 732-13665-1-ND
U3: BQ24040; DSQ0010A
U4: BQ51013B; RHL0020A
VR1: RT8020RT8020GQW; SON45P300X300X80-13T160X250N
XR19: 10k; 0402_RES; MPN RC0402JR-0710KL; DIGIKEY 311-10KJRCT-ND

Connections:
!CHG: U3.8 (!CHG), U4.7 (!CHG); also elsewhere on the board
!PG: U3.5 (!PG); also elsewhere on the board
+1V8: C8.P$2 (2), C46.1, JP11.1, L2.P$1 (1), R29.1; also elsewhere on the board
+2V5: C7.P$1 (1), C47.2, JP10.1, L1.P$2 (2), R28.2; also elsewhere on the board
BATIN: C27.1, R30.2, R31.1; also elsewhere on the board
BATT_THERM: J4.2, J4.2SUPP (2), JP2.3
BATT_TS: JP2.2, U3.9 (TS)
BQ_AC1: C9.1, C10.1, C15.2, C17.1, C18.1, C19.1, C20.2, C38.2, U4.2 (AC1)
BQ_AC2: C9.2, C10.2, C16.2, C21.2, C39.2, L4.P$2 (2), U4.19 (AC2)
BQ_BOOT1: C15.1, U4.3 (BOOT1)
BQ_BOOT2: C16.1, U4.17 (BOOT2)
BQ_CLAMP1: C38.1, U4.5 (CLAMP1)
BQ_CLAMP2: C39.1, U4.16 (CLAMP2)
BQ_COMM1: C20.1, U4.6 (COMM1)
BQ_COMM2: C21.1, U4.15 (COMM2)
BQ_FOD: R7.1, R9.2, R23.2, U4.14 (FOD)
BQ_ILM: R8.1, U4.12 (ILIM)
BQ_ISET: R15.2, U3.2 (ISET)
BQ_RECT: C28.1, C56.1, C57.1, R18.1, U4.18 (RECT)
COIL_AC1: C17.2, C18.2, C19.2, L4.P$1 (1)
GND: C27.2, C28.2, C29.2, C30.2, C41.2, C42.2, C45.1, C46.2, C47.1, C48.2, C53.2, C56.2, C57.2, J4.1, J4.1SUPP (1), JP9.2, R6.2, R14.1, R15.1, R26.1, R27.1, R30.1, RX7.1, U3.3 (VSS), U3.7 (ISET2), U3.PAD (VSS), U4.1 (PGND), U4.9 (AD), U4.10 (EN1), U4.11 (EN2), U4.20 (PGND), U4.PAD (PGND), VR1.3 (GND2), VR1.9 (GND1), VR1.13 (GND2), XR19.1; also elsewhere on the board
unnamed: R6.1, R7.2
unnamed: JP2.1, XR19.2
unnamed: RX7.2, U3.4 (PRETERM)
unnamed: R18.2, R23.1
unnamed: R8.2, R9.1
unnamed: R13.2, RT1.1
unnamed: R13.1, R14.2
QI_TS_CTRL: C30.1, RT1.2, U4.13 (TS/CTRL); also elsewhere on the board
VBAT: C42.1, J4.3, J4.3SUPP (3), JP9.1, S1.2, U3.10 (OUT)
VBAT_SWITCHED: C45.2, C48.1, R31.2, S1.3, VR1.1 (VIN2), VR1.6 (EN1), VR1.7 (VIN1), VR1.12 (EN2); also elsewhere on the board
VQI: C29.1, C41.1, C53.1, U3.1 (IN), U4.4 (OUT)
VR1_FB1: C8.P$1 (1), R27.2, R29.2, VR1.4 (FB1)
VR1_FB2: C7.P$2 (2), R26.2, R28.1, VR1.10 (FB2)
VR1_LX1: L2.P$2 (2), VR1.8 (LX1)
VR1_LX2: L1.P$1 (1), VR1.2 (LX2)

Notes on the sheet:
2.5V Rail DW.VDD2 88 mA (100) 9DOF 12.3 mA (15) Buzzer 90 mA (150) ------------------------ 190.3 mA (265) 40%I->L: 6.5 uH ( 9.2) ∆IL 85 mA (120) COUT=4.7uF, ESR@1.5MHz=0.005 ∆Vout 1.9 mV ( 2.7) ** After ^math, moved the VDDAUDA LDO from battery to hang off 2.5V for routing [plus some eff win I gue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
1.8V Rail DW.VDD1 10 mA (10) DW.VDD3 70 mA (100) Flash 35 mA (50) 9DOF 12.3 mA (15) Apollo4 11.3 mA (120) ------------------------ 141.6 (295) 40%I->L: 5.8 uH ( 11.3) ∆IL 68 mA (132) COUT=4.7uF, ESR@1.5MHz=0.005 ∆Vout 1.5 mV ( 3)
Vout = Vref * (1 + R1/R2) Vref=0.6V, R1=850kΩ R2 = 850e3/((2.5/.6)-1) = 268.4kΩ R2 = 850e3/((1.875/.6)-1) = 400.0kΩ Note: 1.8 -> 1.875 to balance buffer above 1.8~1.85 for AP4 and below the hard max of 1.95 for the flash chip
Switch Current Rating: 250 mA (Assume 90% eff) 2.5: (150*2.5)/(3.4*.9) = 125 1.8: (200*1.8)/(3.4*.9) = 120
Actual: 402k -> 1.8687V
Actual: 261k -> 2.554V

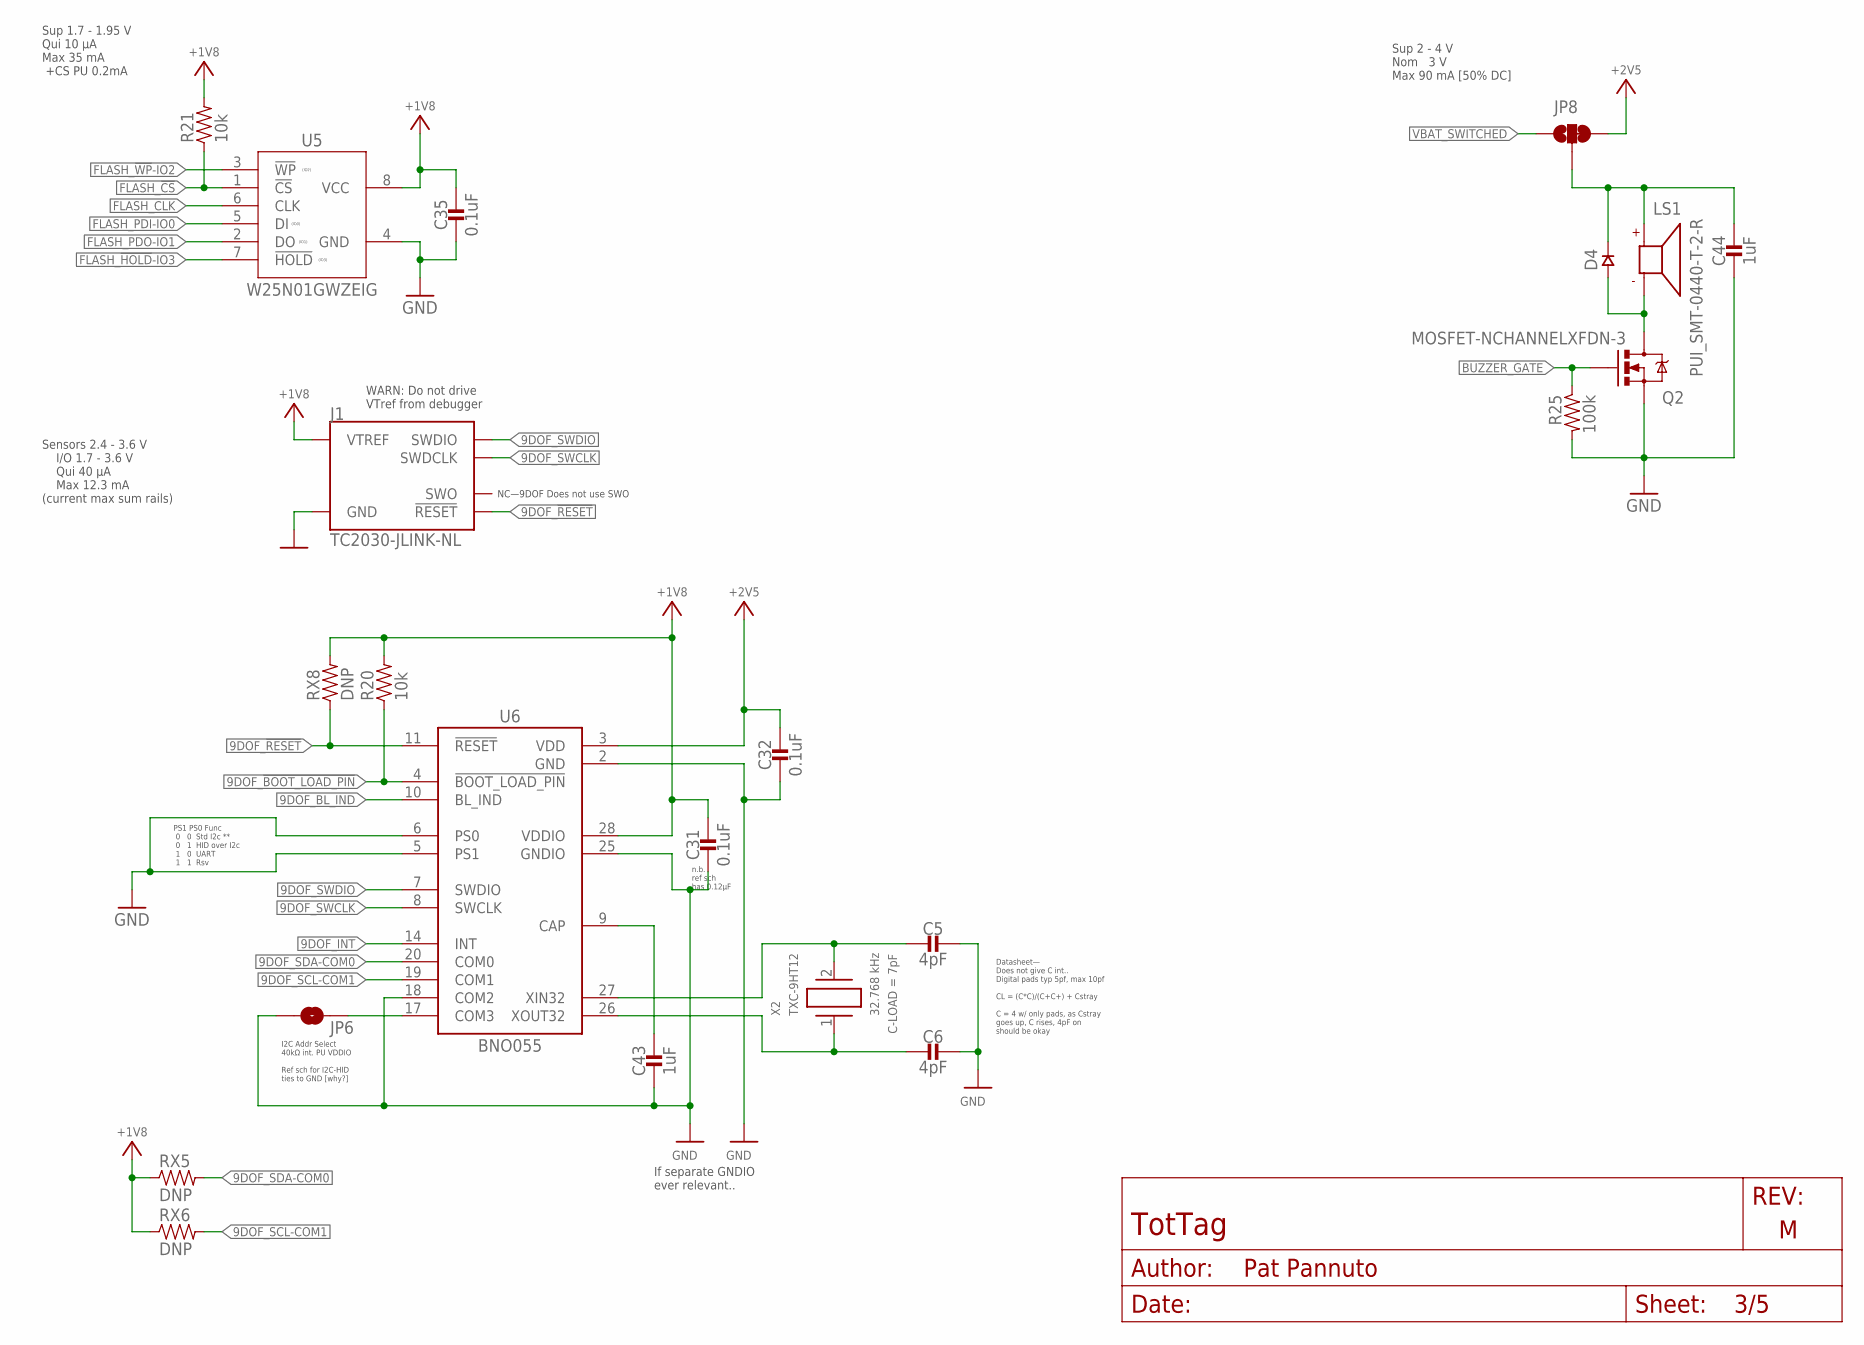
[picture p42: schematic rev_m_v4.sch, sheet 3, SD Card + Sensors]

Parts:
C5, C6: 4pF; 0201_CAP; MPN GRM0335C1H4R0BA01D
C31, C32, C35: 0.1uF; 0402_CAP; MPN CL05A104KP5NNNC
C43, C44: 1uF; 0402_CAP; MPN GRM155R70J105KA12J
D4: DIODE0402; 0402_DIODE; MPN CDSQR400B-HF; DIGIKEY 641-2087-1-ND
J1: TC2030-JLINK-NL; TC2030-IDC-NL
JP6: JUMPER-SMT_2_NO_SILK; SMT-JUMPER_2_NO_SILK
JP8: JUMPER-SMT_3_1-NC_TRACE_SILK; SMT-JUMPER_3_1-NC_TRACE_SILK
LS1: PUI_SMT-0440-T-2-R; SMT-0440-T-2-R
Q2: MOSFET-NCHANNELXFDN-3; XFDFN-3
R20, R21: 10k; 0402_RES; MPN RC0402JR-0710KL; DIGIKEY 311-10KJRCT-ND
R25: 100k; 0402_RES; MPN RT0402BRE07100KL
RX5, RX6, RX8: DNP; 0603-RES
U5: W25N01GWZEIG; WSON127P800X600X80-9T430X340N
U6: BNO055; LGA28R0P510X4_5P2X3P8X1
X2: TXC-9HT12; MPN 9HT12-32.768KDZY-T

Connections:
9DOF_!BOOT_LOAD_PIN: R20.1, U6.4 (!BOOT_LOAD_PIN); also elsewhere on the board
9DOF_!RESET: J1.3 (!RESET), RX8.1, U6.11 (!RESET); also elsewhere on the board
9DOF_BL_IND: U6.10 (BL_IND); also elsewhere on the board
9DOF_CAP: C43.1, U6.9 (CAP)
9DOF_INT: U6.14 (INT); also elsewhere on the board
9DOF_SCL-COM1: RX6.2, U6.19 (COM1); also elsewhere on the board
9DOF_SDA-COM0: RX5.2, U6.20 (COM0); also elsewhere on the board
9DOF_SWCLK: J1.4 (SWDCLK), U6.8 (SWCLK)
9DOF_SWDIO: J1.2 (SWDIO), U6.7 (SWDIO)
9DOF_XI: C5.P$2 (2), U6.27 (XIN32), X2.2
9DOF_XO: C6.P$2 (2), U6.26 (XOUT32), X2.1
+1V8: C31.1, C35.1, J1.1 (VTREF), R20.2, R21.2, RX5.1, RX6.1, RX8.2, U5.8 (VCC), U6.28 (VDDIO); also elsewhere on the board
+2V5: C32.1, JP8.3, U6.3 (VDD); also elsewhere on the board
BUZZER_GATE: Q2.G, R25.1; also elsewhere on the board
BUZZER_SUPPLY: C44.1, D4.CATHODE, JP8.2, LS1.+
FLASH_!CS: R21.1, U5.1 (!CS); also elsewhere on the board
FLASH_!HOLD!-IO3: U5.7 (!HOLD); also elsewhere on the board
FLASH_!WP!-IO2: U5.3 (!WP); also elsewhere on the board
FLASH_CLK: U5.6 (CLK); also elsewhere on the board
FLASH_PDI-IO0: U5.5 (DI); also elsewhere on the board
FLASH_PDO-IO1: U5.2 (DO); also elsewhere on the board
GND: C5.P$1 (1), C6.P$1 (1), C31.2, C32.2, C35.2, C43.2, C44.2, J1.5 (GND), JP6.1, Q2.S, R25.2, U5.4 (GND), U6.2 (GND), U6.5 (PS1), U6.6 (PS0), U6.18 (COM2), U6.25 (GNDIO); also elsewhere on the board
unnamed: D4.ANODE, LS1.- (N), Q2.D
unnamed: JP6.2, U6.17 (COM3)
VBAT_SWITCHED: JP8.1; also elsewhere on the board

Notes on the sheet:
Sup 1.7 - 1.95 V Qui 10 µA Max 35 mA +CS PU 0.2mA
Sensors 2.4 - 3.6 V I/O 1.7 - 3.6 V Qui 40 µA Max 12.3 mA (current max sum rails)
Sup 2 - 4 V Nom 3 V Max 90 mA [50% DC]
PS1 PS0 Func 0 0 Std I2c ** 0 1 HID over I2c 1 0 UART 1 1 Rsv
If separate GNDIO ever relevant..
I2C Addr Select 40kΩ int. PU VDDIO Ref sch for I2C-HID ties to GND [why?]
n.b. ref sch has 0.12µF
WARN: Do not drive VTref from debugger
Datasheet— Does not give C int.. Digital pads typ 5pf, max 10pf CL = (C*C)/(C+C+) + Cstray C = 4 w/ only pads, as Cstray goes up, C rises, 4pF on should be okay
NC—9DOF Does not use SWO

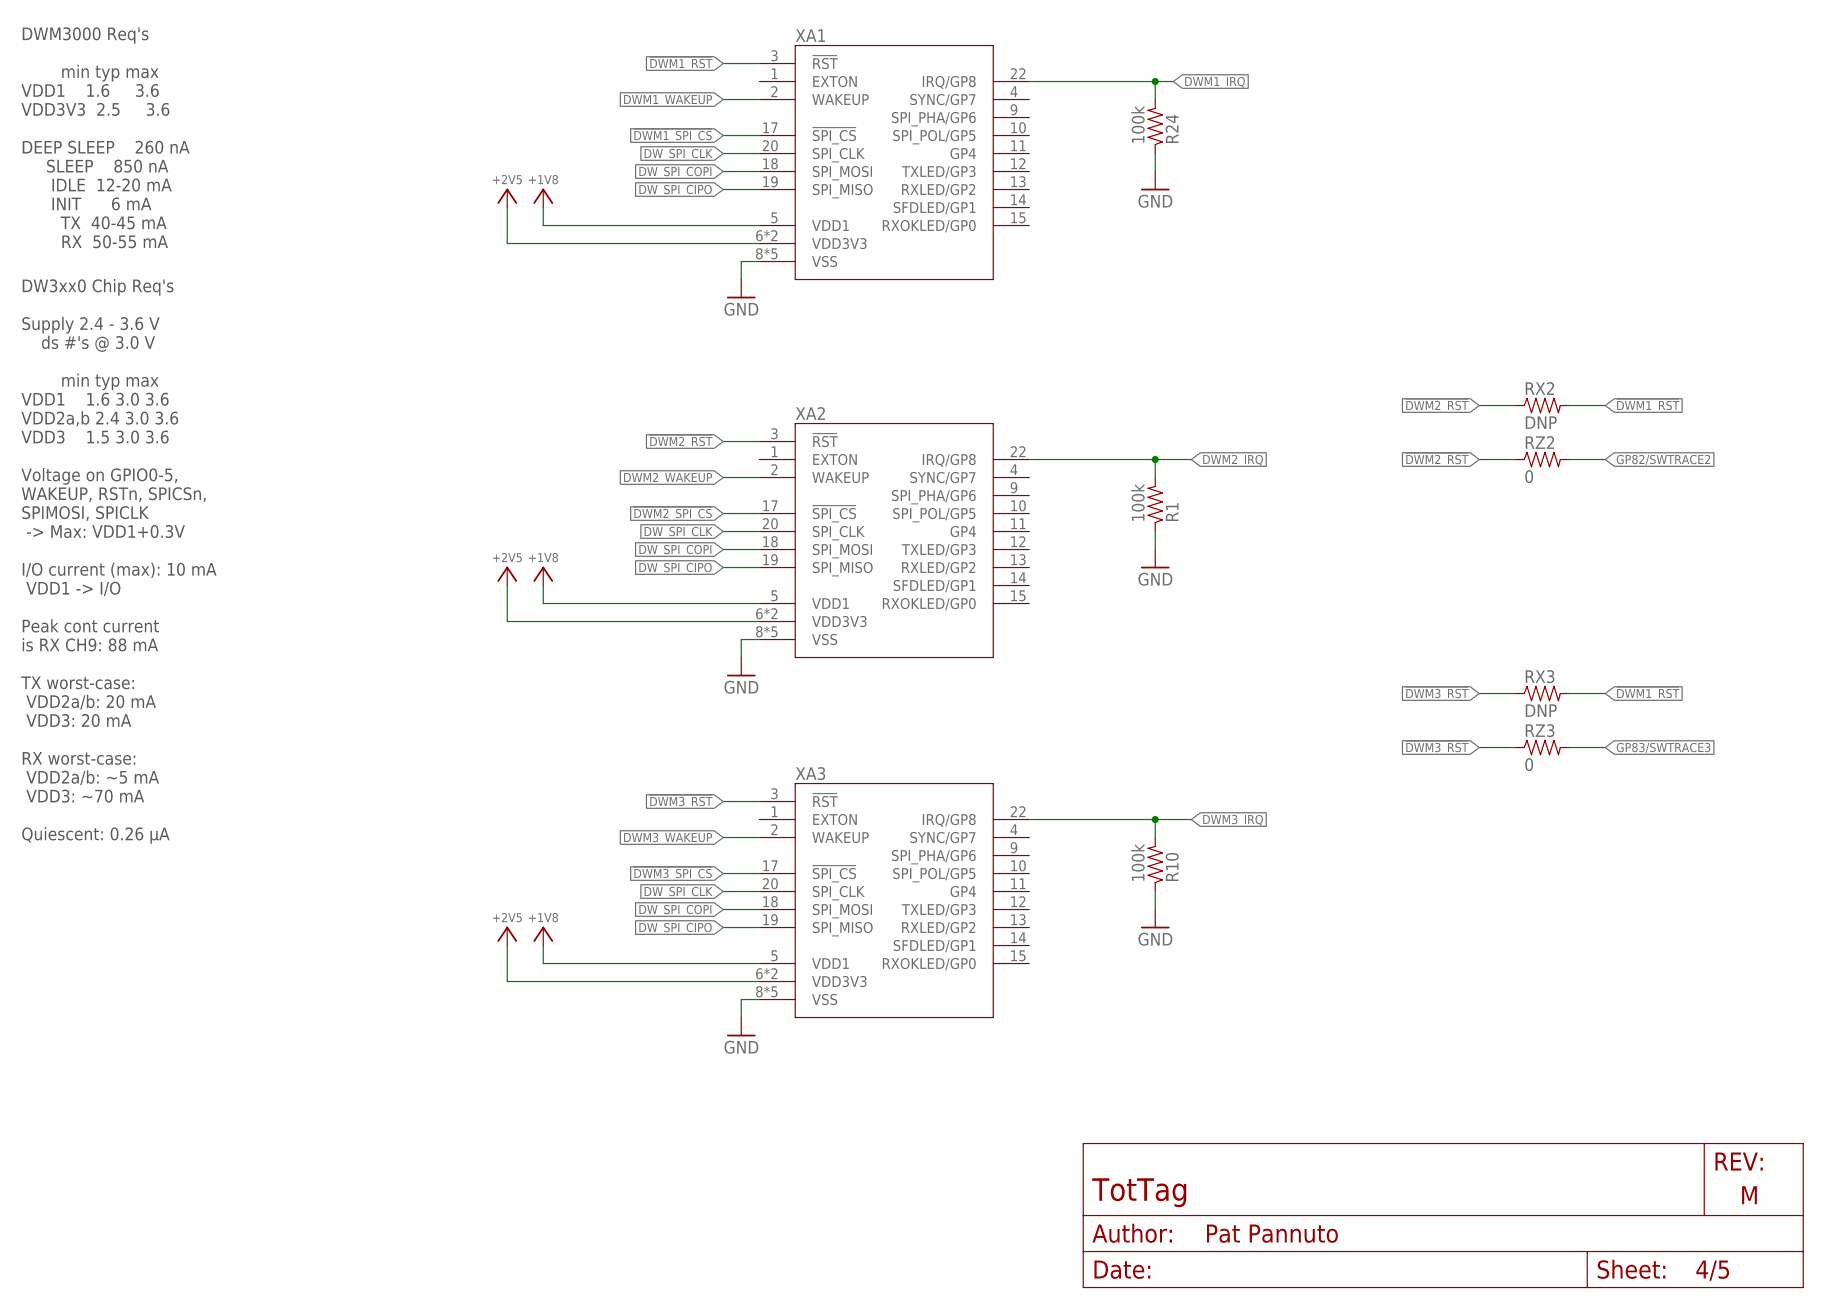
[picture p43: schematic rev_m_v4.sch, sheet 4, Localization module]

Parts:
R1, R10, R24: 100k; 0402_RES; MPN RT0402BRE07100KL
RX2, RX3: DNP; 0603-RES
RZ2, RZ3: 0; 0603-RES; MPN RMCF0603ZT0R00
XA1, XA2, XA3: DWM3000

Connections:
!DWM1_RST: RX2.2, RX3.2, XA1.3 (!RST); also elsewhere on the board
!DWM1_SPI_CS: XA1.17 (!SPI_CS); also elsewhere on the board
!DWM2_RST: RX2.1, RZ2.1, XA2.3 (!RST)
!DWM2_SPI_CS: XA2.17 (!SPI_CS); also elsewhere on the board
!DWM3_RST: RX3.1, RZ3.1, XA3.3 (!RST)
!DWM3_SPI_CS: XA3.17 (!SPI_CS); also elsewhere on the board
+1V8: XA1.5 (VDD1), XA2.5 (VDD1), XA3.5 (VDD1); also elsewhere on the board
+2V5: XA1.6 (VDD3V3), XA1.7 (VDD3V3), XA2.6 (VDD3V3), XA2.7 (VDD3V3), XA3.6 (VDD3V3), XA3.7 (VDD3V3); also elsewhere on the board
DWM1_IRQ: R24.2, XA1.22 (IRQ/GP8); also elsewhere on the board
DWM1_WAKEUP: XA1.2 (WAKEUP); also elsewhere on the board
DWM2_IRQ: R1.2, XA2.22 (IRQ/GP8); also elsewhere on the board
DWM2_WAKEUP: XA2.2 (WAKEUP); also elsewhere on the board
DWM3_IRQ: R10.2, XA3.22 (IRQ/GP8); also elsewhere on the board
DWM3_WAKEUP: XA3.2 (WAKEUP); also elsewhere on the board
DW_SPI_CIPO: XA1.19 (SPI_MISO), XA2.19 (SPI_MISO), XA3.19 (SPI_MISO); also elsewhere on the board
DW_SPI_CLK: XA1.20 (SPI_CLK), XA2.20 (SPI_CLK), XA3.20 (SPI_CLK); also elsewhere on the board
DW_SPI_COPI: XA1.18 (SPI_MOSI), XA2.18 (SPI_MOSI), XA3.18 (SPI_MOSI); also elsewhere on the board
GND: R1.1, R10.1, R24.1, XA1.8 (VSS), XA1.16 (VSS), XA1.21 (VSS), XA1.23 (VSS), XA1.24 (VSS), XA2.8 (VSS), XA2.16 (VSS), XA2.21 (VSS), XA2.23 (VSS), XA2.24 (VSS), XA3.8 (VSS), XA3.16 (VSS), XA3.21 (VSS), XA3.23 (VSS), XA3.24 (VSS); also elsewhere on the board
GP82/SWTRACE2: RZ2.2; also elsewhere on the board
GP83/SWTRACE3: RZ3.2; also elsewhere on the board

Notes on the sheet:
DW3xx0 Chip Req's Supply 2.4 - 3.6 V ds #'s @ 3.0 V min typ max VDD1 1.6 3.0 3.6 VDD2a,b 2.4 3.0 3.6 VDD3 1.5 3.0 3.6 Voltage on GPIO0-5, WAKEUP, RSTn, SPICSn, SPIMOSI, SPICLK -> Max: VDD1+0.3V I/O current (max): 10 mA VDD1 -> I/O Peak cont current is RX CH9: 88 mA TX worst-case: VDD2a/b: 20 mA VDD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
DWM3000 Req's min typ max VDD1 1.6 3.6 VDD3V3 2.5 3.6 DEEP SLEEP 260 nA SLEEP 850 nA IDLE 12-20 mA INIT 6 mA TX 40-45 mA RX 50-55 mA

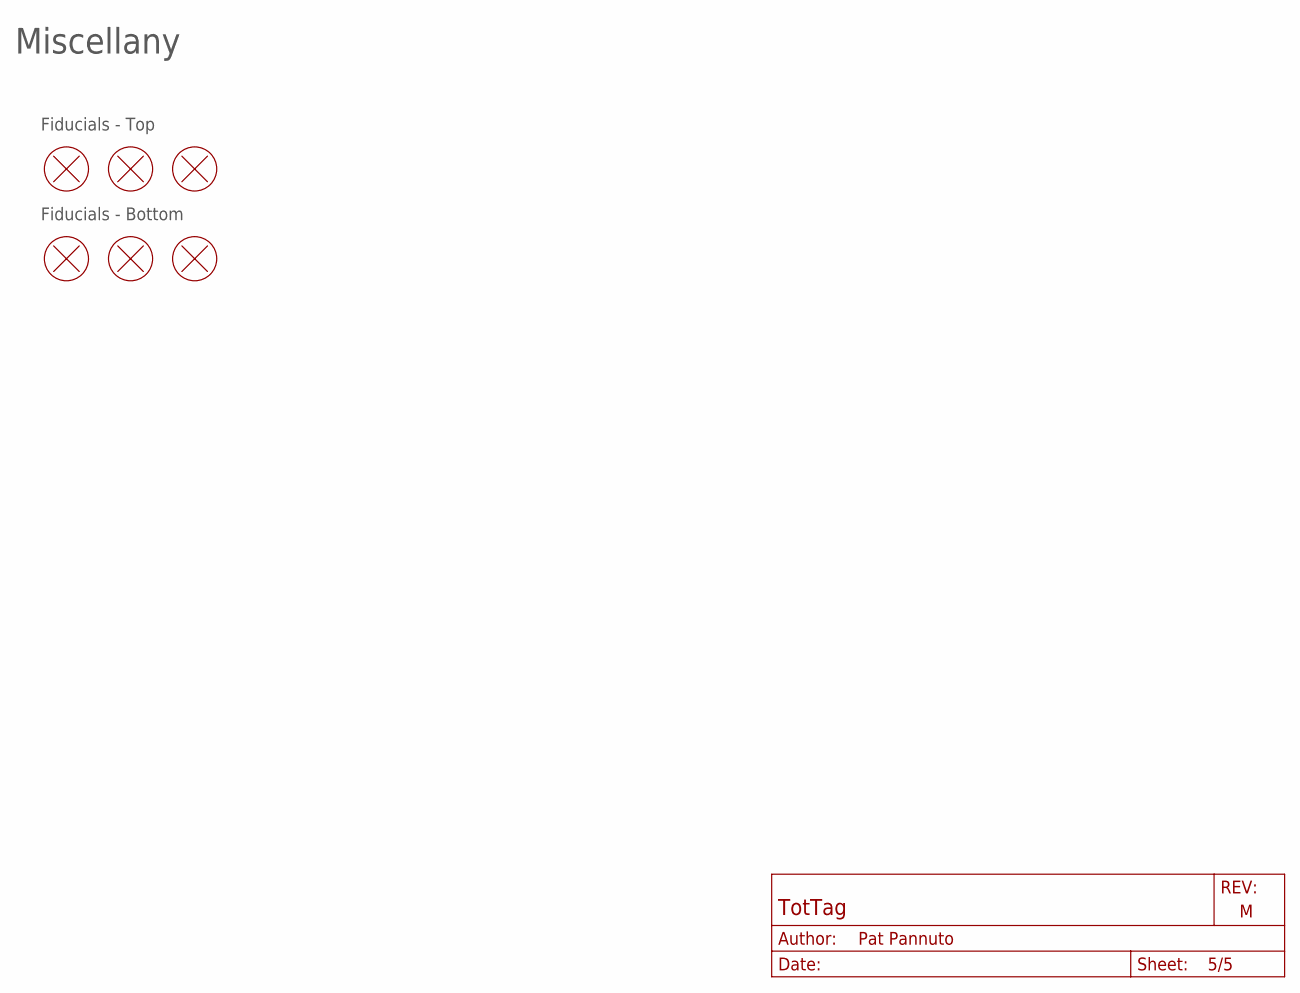
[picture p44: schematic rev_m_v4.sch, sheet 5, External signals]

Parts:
FD1, FD2, FD3, FD4, FD5, FD6: FIDUCIAL; FIDUCIAL_1MM-CU_2MM-MASK

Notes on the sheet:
Miscellany
Fiducials - Top
Fiducials - Bottom

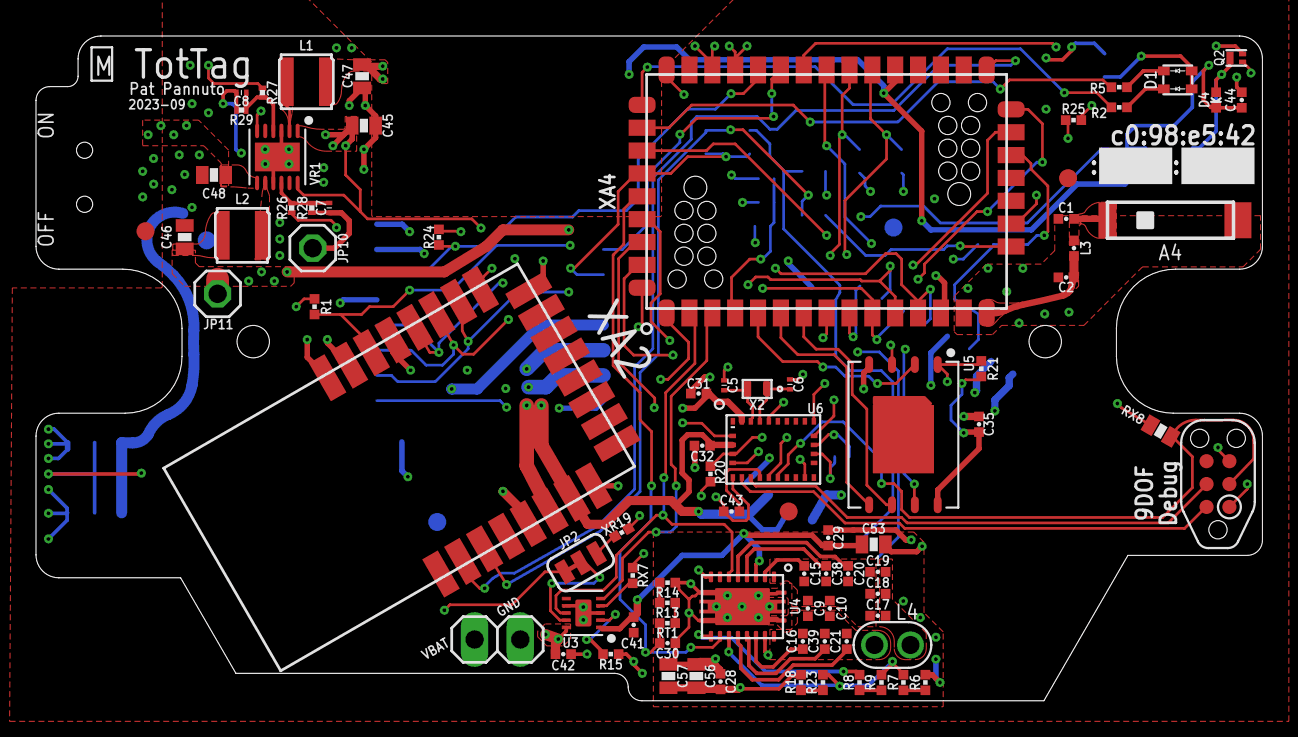
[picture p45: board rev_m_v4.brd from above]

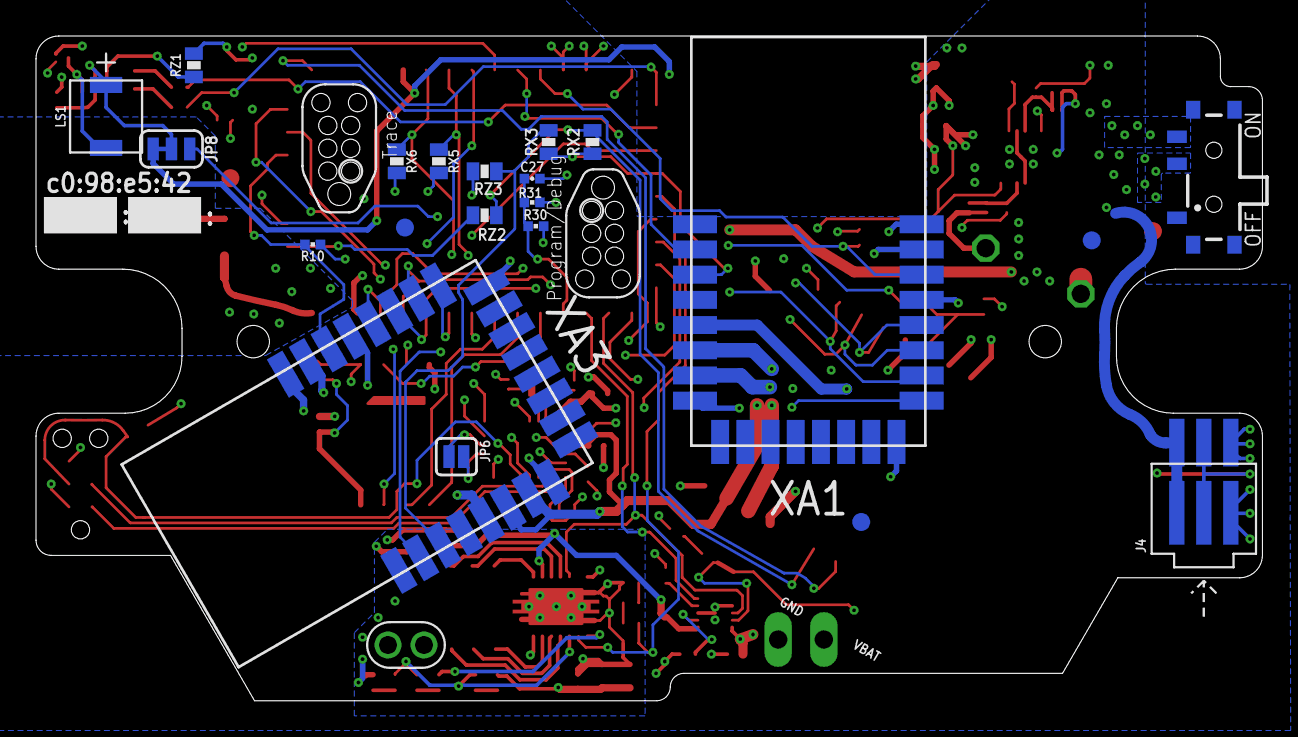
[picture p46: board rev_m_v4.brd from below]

Board: 4 copper layers, 68.1 x 36.9 mm, 103 parts (21 on the bottom side), 82 nets.

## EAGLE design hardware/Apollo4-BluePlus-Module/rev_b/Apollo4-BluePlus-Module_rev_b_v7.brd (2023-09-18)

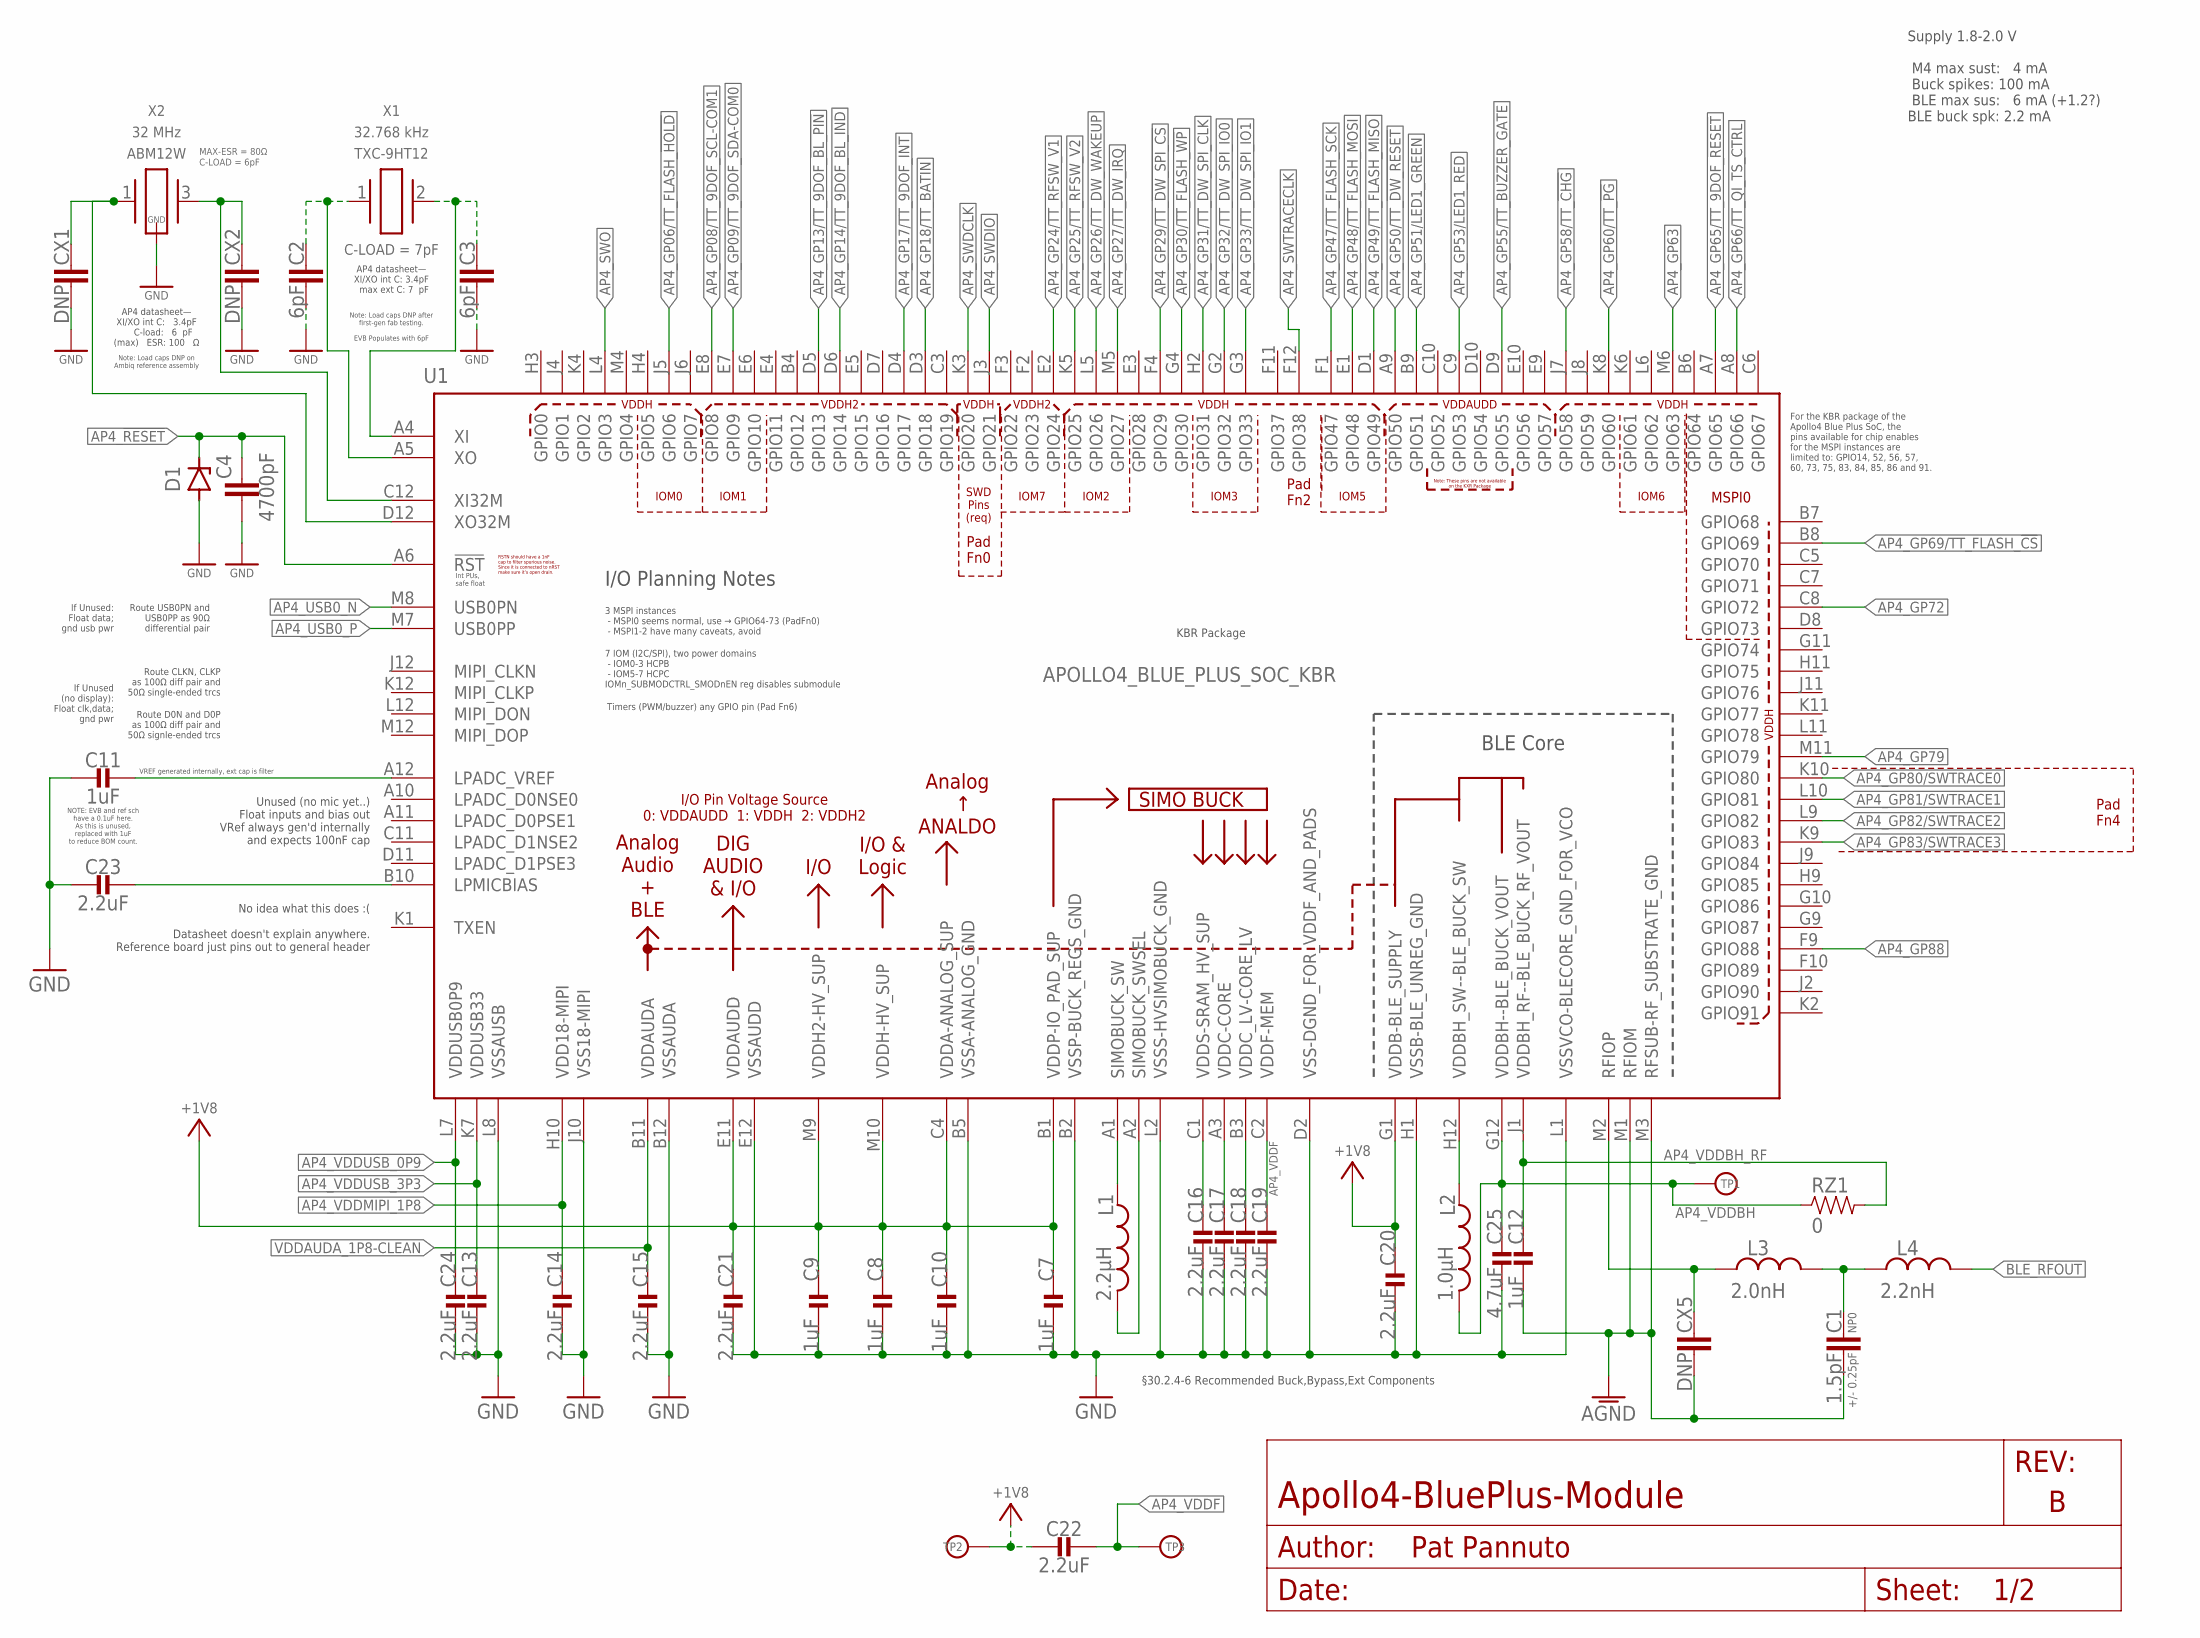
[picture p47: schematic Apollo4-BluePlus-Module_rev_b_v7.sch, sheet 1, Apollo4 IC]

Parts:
C1: 1.5pF; CAPC1005X60; TOLERANCE +/- 0.25pF; MPN C0402C159C5GAC7867
C2, C3: 6pF; CAPC1005X60; MPN GCM1555C1H6R0BA16D
C4: 4700pF; CAPC1005X60; MPN KGM05AR71E472KH
C7, C8, C9, C10, C11, C12: 1uF; 0201_CAP; MPN GRM033R61A105ME44D
C13, C14, C15, C16, C17, C18, C19, C20, C21, C22, C23, C24: 2.2uF; 0201_CAP; MPN GRM033R61A225KE47D
C25: 4.7uF; 0402_CAP; MPN CL05A475MP5NRNC
CX1, CX2, CX5: DNP; CAPC1005X60
D1: ZENER; SODFL1608X70; MPN PESD5V0X1UB,135
L1: 2.2µH; 0805_CAP; MPN DFE201210U-2R2M=P2
L2: 1.0µH; 0603_CAP; MPN DFE18SAN1R0ME0L
L3: 2.0nH; INDC1006X60N; TOLERANCE +/- 0.1 nH; MPN CTTF0402F-2N0B
L4: 2.2nH; INDC1006X60N; TOLERANCE +/- 0.1 nH; MPN CTTF0402F-2N2B
RZ1: 0; 0402_RES; MPN RMCF0402ZT0R00
TP1: VDDBH; PAD.03X.03
TP2: VDDP; PAD.03X.03
TP3: VDDF; PAD.03X.03
U1: APOLLO4_BLUE_PLUS_SOC_KBR; APOLLO4_BLUE_SOC_BGA
X1: TXC-9HT12; MPN 9HT12-32.768KDZY-T
X2: ABM12W; MPN ABM12W-32.0000MHZ-6-D1X-T3

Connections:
+1V8: C7.P$1 (1), C8.P$1 (1), C9.P$1 (1), C10.P$1 (1), C20.P$1 (1), C21.P$1 (1), C22.P$2 (2), TP2.P$1, U1.B1 (VDDP-IO_PAD_SUP), U1.C4 (VDDA-ANALOG_SUP), U1.E11 (VDDAUDD), U1.G1 (VDDB-BLE_SUPPLY), U1.M9 (VDDH2-HV_SUP), U1.M10 (VDDH-HV_SUP); also elsewhere on the board
AGND: C1.2, C12.P$2 (2), CX5.2, U1.M1 (RFIOM), U1.M3 (RFSUB-RF_SUBSTRATE_GND); also elsewhere on the board
AP4_!RESET: C4.1, D1.1 (C), U1.A6 (!RST); also elsewhere on the board
AP4_GP06/TT_FLASH_!HOLD: U1.J5 (GPIO6); also elsewhere on the board
AP4_GP08/TT_9DOF_SCL-COM1: U1.E8 (GPIO8); also elsewhere on the board
AP4_GP09/TT_9DOF_SDA-COM0: U1.E7 (GPIO9); also elsewhere on the board
AP4_GP13/TT_9DOF_!BL_PIN: U1.D5 (GPIO13); also elsewhere on the board
AP4_GP14/TT_9DOF_BL_IND: U1.D6 (GPIO14); also elsewhere on the board
AP4_GP17/TT_9DOF_INT: U1.D4 (GPIO17); also elsewhere on the board
AP4_GP18/TT_BATIN: U1.D3 (GPIO18); also elsewhere on the board
AP4_GP24/TT_RFSW_V1: U1.E2 (GPIO24); also elsewhere on the board
AP4_GP25/TT_RFSW_V2: U1.K5 (GPIO25); also elsewhere on the board
AP4_GP26/TT_DW_WAKEUP: U1.L5 (GPIO26); also elsewhere on the board
AP4_GP27/TT_DW_IRQ: U1.M5 (GPIO27); also elsewhere on the board
AP4_GP29/TT_!DW_SPI_CS: U1.F4 (GPIO29); also elsewhere on the board
AP4_GP30/TT_FLASH_!WP: U1.G4 (GPIO30); also elsewhere on the board
AP4_GP31/TT_DW_SPI_CLK: U1.H2 (GPIO31); also elsewhere on the board
AP4_GP32/TT_DW_SPI_IO0: U1.G2 (GPIO32); also elsewhere on the board
AP4_GP33/TT_DW_SPI_IO1: U1.G3 (GPIO33); also elsewhere on the board
AP4_GP47/TT_FLASH_SCK: U1.F1 (GPIO47); also elsewhere on the board
AP4_GP48/TT_FLASH_MOSI: U1.E1 (GPIO48); also elsewhere on the board
AP4_GP49/TT_FLASH_MISO: U1.D1 (GPIO49); also elsewhere on the board
AP4_GP50/TT_!DW_RESET: U1.A9 (GPIO50); also elsewhere on the board
AP4_GP51/LED1_GREEN: U1.B9 (GPIO51); also elsewhere on the board
AP4_GP53/LED1_RED: U1.C9 (GPIO53); also elsewhere on the board
AP4_GP55/TT_BUZZER_GATE: U1.D9 (GPIO55); also elsewhere on the board
AP4_GP58/TT_!CHG: U1.J7 (GPIO58); also elsewhere on the board
AP4_GP60/TT_!PG: U1.K8 (GPIO60); also elsewhere on the board
AP4_GP63: U1.M6 (GPIO63); also elsewhere on the board
AP4_GP65/TT_9DOF_!RESET: U1.A7 (GPIO65); also elsewhere on the board
AP4_GP66/TT_QI_TS_CTRL: U1.A8 (GPIO66); also elsewhere on the board
AP4_GP69/TT_FLASH_!CS: U1.B8 (GPIO69); also elsewhere on the board
AP4_GP72: U1.C8 (GPIO72); also elsewhere on the board
AP4_GP79: U1.M11 (GPIO79); also elsewhere on the board
AP4_GP80/SWTRACE0: U1.K10 (GPIO80); also elsewhere on the board
AP4_GP81/SWTRACE1: U1.L10 (GPIO81); also elsewhere on the board
AP4_GP82/SWTRACE2: U1.L9 (GPIO82); also elsewhere on the board
AP4_GP83/SWTRACE3: U1.K9 (GPIO83); also elsewhere on the board
AP4_GP88: U1.F9 (GPIO88); also elsewhere on the board
AP4_LPADC_VREF: C11.P$2 (2), U1.A12 (LPADC_VREF)
AP4_LPMICBIAS: C23.P$2 (2), U1.B10 (LPMICBIAS)
AP4_RFIOP: CX5.1, L3.1, U1.M2 (RFIOP)
AP4_SWDCLK: U1.K3 (GPIO20); also elsewhere on the board
AP4_SWDIO: U1.J3 (GPIO21); also elsewhere on the board
AP4_SWO: U1.L4 (GPIO3); also elsewhere on the board
AP4_SWTRACECLK: U1.F12 (GPIO38); also elsewhere on the board
AP4_USB0_N: U1.M8 (USB0PN); also elsewhere on the board
AP4_USB0_P: U1.M7 (USB0PP); also elsewhere on the board
AP4_VDDBH: C25.1, L2.2, RZ1.1, TP1.P$1, U1.G12 (VDDBH--BLE_BUCK_VOUT)
AP4_VDDBH_RF: C12.P$1 (1), RZ1.2, U1.J1 (VDDBH_RF--BLE_BUCK_RF_VOUT)
AP4_VDDBH_SW: L2.1, U1.H12 (VDDBH_SW--BLE_BUCK_SW)
AP4_VDDC: C17.P$1 (1), U1.A3 (VDDC-CORE)
AP4_VDDC_LV: C18.P$1 (1), U1.B3 (VDDC_LV-CORE_LV)
AP4_VDDF: C19.P$1 (1), C22.P$1 (1), TP3.P$1, U1.C2 (VDDF-MEM)
AP4_VDDMIPI_1P8: C14.P$1 (1), U1.H10 (VDD18-MIPI); also elsewhere on the board
AP4_VDDS: C16.P$1 (1), U1.C1 (VDDS-SRAM_HV_SUP)
AP4_VDDUSB_0P9: C24.P$1 (1), U1.L7 (VDDUSB0P9); also elsewhere on the board
AP4_VDDUSB_3P3: C13.P$1 (1), U1.K7 (VDDUSB33); also elsewhere on the board
AP4_XI: C3.1, U1.A4 (XI), X1.2
AP4_XI32M: CX2.1, U1.C12 (XI32M), X2.3 (2)
AP4_XO: C2.1, U1.A5 (XO), X1.1
AP4_XO32M: CX1.1, U1.D12 (XO32M), X2.1
BLE_RFOUT: L4.2; also elsewhere on the board
GND: C2.2, C3.2, C4.2, C7.P$2 (2), C8.P$2 (2), C9.P$2 (2), C10.P$2 (2), C11.P$1 (1), C13.P$2 (2), C14.P$2 (2), C15.P$2 (2), C16.P$2 (2), C17.P$2 (2), C18.P$2 (2), C19.P$2 (2), C20.P$2 (2), C21.P$2 (2), C23.P$1 (1), C24.P$2 (2), C25.2, CX1.2, CX2.2, D1.2 (A), U1.B2 (VSSP-BUCK_REGS_GND), U1.B5 (VSSA-ANALOG_GND), U1.B12 (VSSAUDA), U1.D2 (VSS-DGND_FOR_VDDF_AND_PADS), U1.E12 (VSSAUDD), U1.H1 (VSSB-BLE_UNREG_GND), U1.J10 (VSS18-MIPI), U1.L1 (VSSVCO-BLECORE_GND_FOR_VCO), U1.L2 (VSSS-HVSIMOBUCK_GND), U1.L8 (VSSAUSB), X2.2 (GND), X2.4 (GND); also elsewhere on the board
unnamed: C1.1, L3.2, L4.1
SIMOBUCK_SW: L1.P$1 (1), U1.A1 (SIMOBUCK_SW)
SIMOBUCK_SWSEL: L1.P$2 (2), U1.A2 (SIMOBUCK_SWSEL)
VDDAUDA_1P8-CLEAN: C15.P$1 (1), U1.B11 (VDDAUDA); also elsewhere on the board

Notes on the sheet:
Supply 1.8-2.0 V M4 max sust: 4 mA Buck spikes: 100 mA BLE max sus: 6 mA (+1.2?) BLE buck spk: 2.2 mA
Note: Load caps DNP on Ambiq reference assembly
Int PUs, safe float
If Unused: Float data; gnd usb pwr
If Unused (no display): Float clk,data; gnd pwr
Unused (no mic yet..) Float inputs and bias out VRef always gen'd internally and expects 100nF cap
No idea what this does :( Datasheet doesn't explain anywhere. Reference board just pins out to general header
I/O Planning Notes
3 MSPI instances - MSPI0 seems normal, use → GPIO64-73 (PadFn0) - MSPI1-2 have many caveats, avoid
7 IOM (I2C/SPI), two power domains - IOM0-3 HCPB - IOM5-7 HCPC IOMn_SUBMODCTRL_SMODnEN reg disables submodule
MSPI0
IOM0
IOM1
Timers (PWM/buzzer) any GPIO pin (Pad Fn6)
KBR Package
For the KBR package of the Apollo4 Blue Plus SoC, the pins available for chip enables for the MSPI instances are limited to: GPIO14, 52, 56, 57, 60, 73, 75, 83, 84, 85, 86 and 91.
§30.2.4-6 Recommended Buck,Bypass,Ext Components
SWD Pins (req)
VREF generated internally, ext cap is filter
IOM3
AP4 datasheet— XI/XO int C: 3.4pF max ext C: 7 pF
AP4 datasheet— XI/XO int C: 3.4pF C-load: 6 pF (max) ESR: 100 Ω
Pad Fn4
Pad Fn2
Pad Fn0
Note: Load caps DNP after first-gen fab testing. EVB Populates with 6pF
Route USB0PN and USB0PP as 90Ω differential pair
Route CLKN, CLKP as 100Ω diff pair and 50Ω single-ended trcs
Route D0N and D0P as 100Ω diff pair and 50Ω signle-ended trcs
NOTE: EVB and ref sch have a 0.1uF here. As this is unused, replaced with 1uF to reduce BOM count.
IOM2
IOM5
IOM6
IOM7

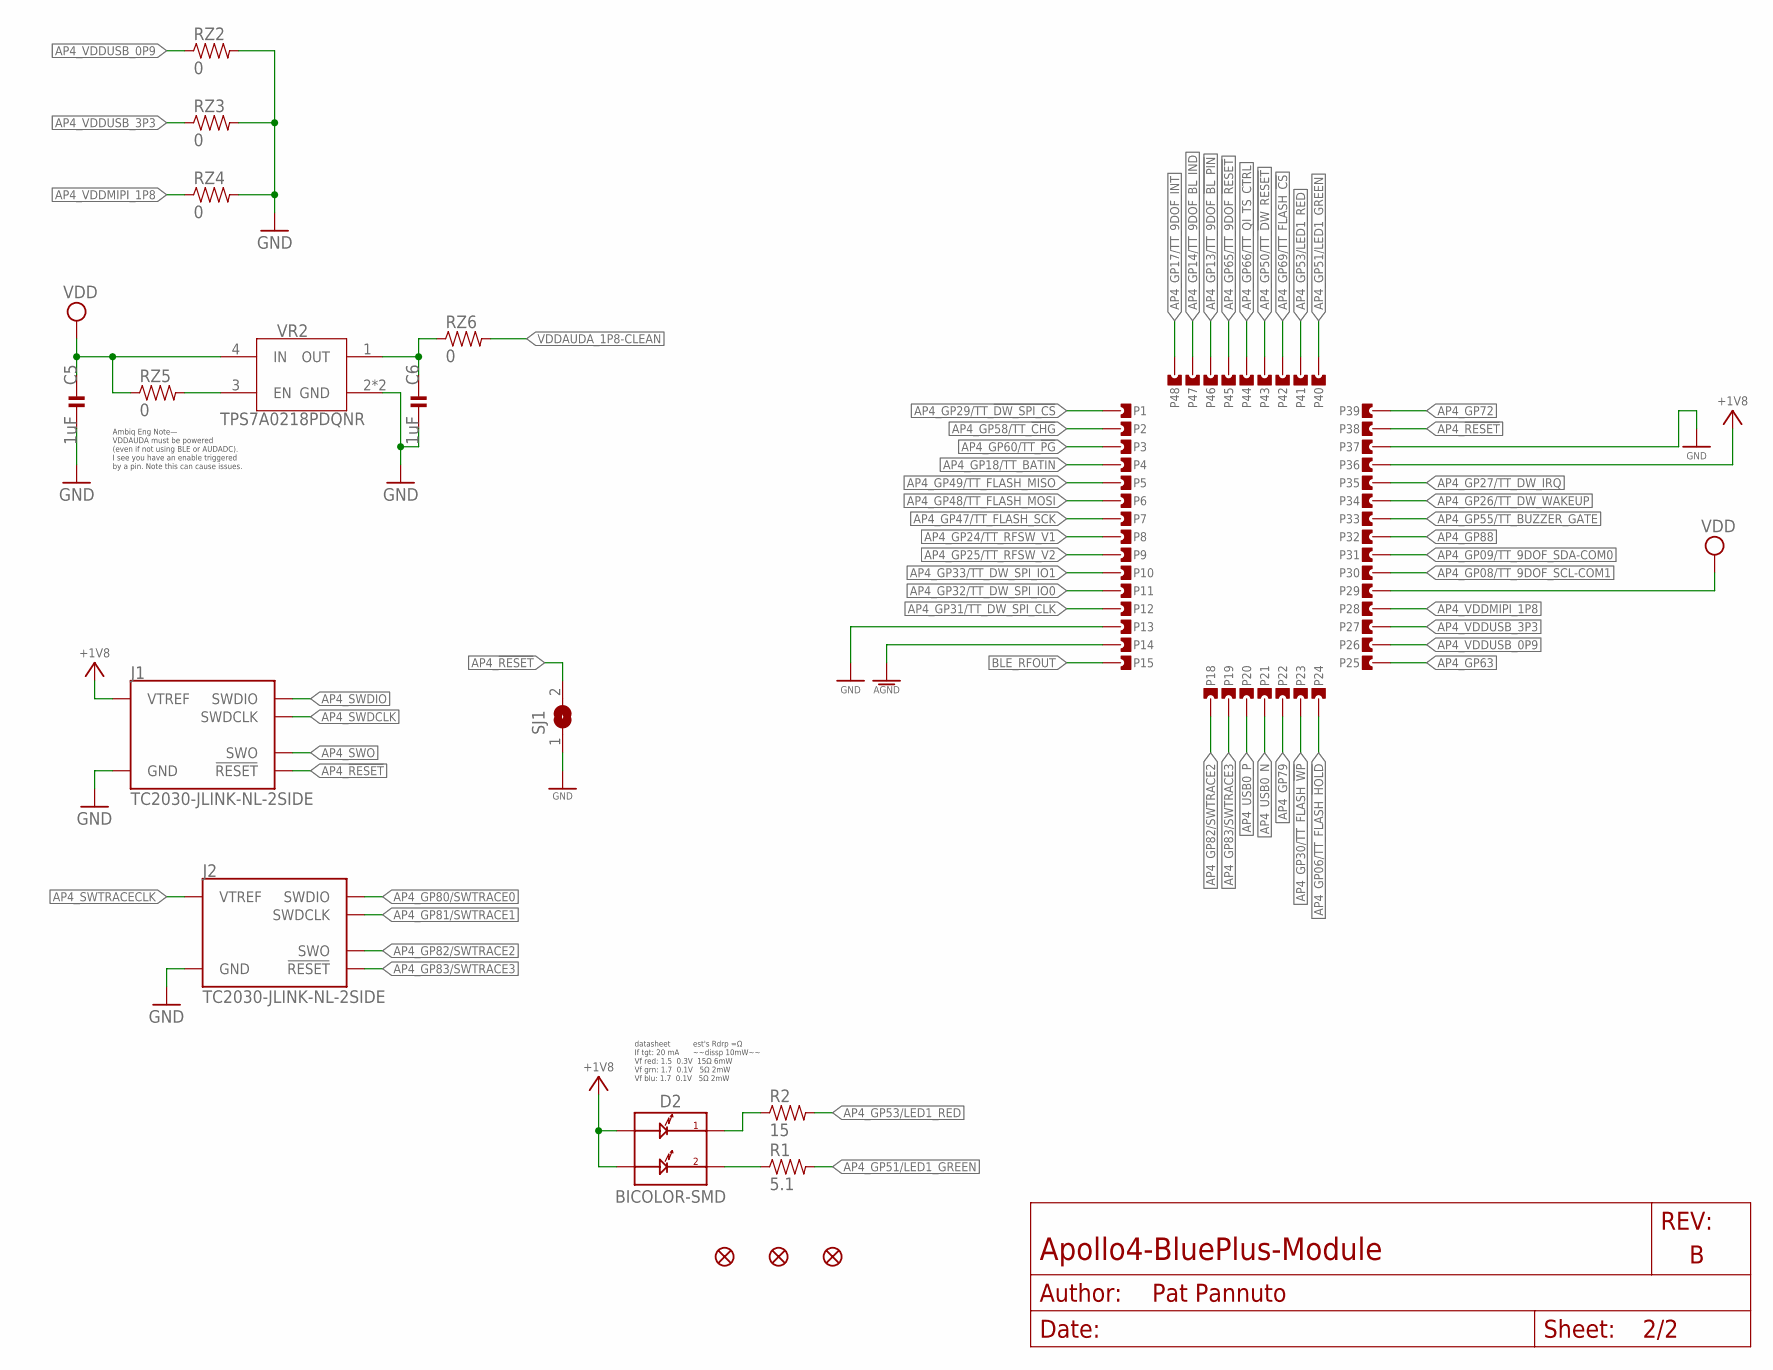
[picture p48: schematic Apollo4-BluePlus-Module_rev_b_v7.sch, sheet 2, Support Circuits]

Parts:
C5, C6: 1uF; 0201_CAP; MPN GRM033R61A105ME44D
D2: BICOLOR-SMD; LED-0606; MPN MCL0606FRD1GR1T
FD1, FD2, FD3: FIDUCIALUFIDUCIAL; FIDUCIAL-MICRO
J1, J2: TC2030-JLINK-NL-2SIDE; TC2030-IDC-NL-2SIDE
P1, P2, P3, P4, P5, P6, P7, P8, P9, P10, P11, P12, P13, P14, P15, P18, P19, P20, P21, P22, P23, P24, P25, P26, P27, P28, P29, P30, P31, P32, P33, P34, P35, P36, P37, P38, P39, P40, P41, P42, P43, P44, P45, P46, P47, P48: CASTELLATION4L; CASTELLATION-0.55MM_DRILL-4L
R1: 5.1; 0201_RES; MPN SR731HTTC5R10F
R2: 15; 0201_RES; MPN ERJ-1GNJ150C
RZ2, RZ3, RZ4, RZ5, RZ6: 0; 0402_RES; MPN RMCF0402ZT0R00
SJ1: SJ
VR2: TPS7A0218PDQNR; 4-XDFN-EP

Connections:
+1V8: D2.A1, D2.A2, J1.1 (VTREF), J1.B1 (VTREF), P36.P$1, P36.P$2, P36.P$3; also elsewhere on the board
AGND: P14.P$1, P14.P$2, P14.P$3; also elsewhere on the board
AP4_!RESET: J1.3 (!RESET), J1.B3 (!RESET), P38.P$1, P38.P$2, P38.P$3, SJ1.2; also elsewhere on the board
AP4_GP06/TT_FLASH_!HOLD: P24.P$1, P24.P$2, P24.P$3; also elsewhere on the board
AP4_GP08/TT_9DOF_SCL-COM1: P30.P$1, P30.P$2, P30.P$3; also elsewhere on the board
AP4_GP09/TT_9DOF_SDA-COM0: P31.P$1, P31.P$2, P31.P$3; also elsewhere on the board
AP4_GP13/TT_9DOF_!BL_PIN: P46.P$1, P46.P$2, P46.P$3; also elsewhere on the board
AP4_GP14/TT_9DOF_BL_IND: P47.P$1, P47.P$2, P47.P$3; also elsewhere on the board
AP4_GP17/TT_9DOF_INT: P48.P$1, P48.P$2, P48.P$3; also elsewhere on the board
AP4_GP18/TT_BATIN: P4.P$1, P4.P$2, P4.P$3; also elsewhere on the board
AP4_GP24/TT_RFSW_V1: P8.P$1, P8.P$2, P8.P$3; also elsewhere on the board
AP4_GP25/TT_RFSW_V2: P9.P$1, P9.P$2, P9.P$3; also elsewhere on the board
AP4_GP26/TT_DW_WAKEUP: P34.P$1, P34.P$2, P34.P$3; also elsewhere on the board
AP4_GP27/TT_DW_IRQ: P35.P$1, P35.P$2, P35.P$3; also elsewhere on the board
AP4_GP29/TT_!DW_SPI_CS: P1.P$1, P1.P$2, P1.P$3; also elsewhere on the board
AP4_GP30/TT_FLASH_!WP: P23.P$1, P23.P$2, P23.P$3; also elsewhere on the board
AP4_GP31/TT_DW_SPI_CLK: P12.P$1, P12.P$2, P12.P$3; also elsewhere on the board
AP4_GP32/TT_DW_SPI_IO0: P11.P$1, P11.P$2, P11.P$3; also elsewhere on the board
AP4_GP33/TT_DW_SPI_IO1: P10.P$1, P10.P$2, P10.P$3; also elsewhere on the board
AP4_GP47/TT_FLASH_SCK: P7.P$1, P7.P$2, P7.P$3; also elsewhere on the board
AP4_GP48/TT_FLASH_MOSI: P6.P$1, P6.P$2, P6.P$3; also elsewhere on the board
AP4_GP49/TT_FLASH_MISO: P5.P$1, P5.P$2, P5.P$3; also elsewhere on the board
AP4_GP50/TT_!DW_RESET: P43.P$1, P43.P$2, P43.P$3; also elsewhere on the board
AP4_GP51/LED1_GREEN: P40.P$1, P40.P$2, P40.P$3, R1.2; also elsewhere on the board
AP4_GP53/LED1_RED: P41.P$1, P41.P$2, P41.P$3, R2.2; also elsewhere on the board
AP4_GP55/TT_BUZZER_GATE: P33.P$1, P33.P$2, P33.P$3; also elsewhere on the board
AP4_GP58/TT_!CHG: P2.P$1, P2.P$2, P2.P$3; also elsewhere on the board
AP4_GP60/TT_!PG: P3.P$1, P3.P$2, P3.P$3; also elsewhere on the board
AP4_GP63: P25.P$1, P25.P$2, P25.P$3; also elsewhere on the board
AP4_GP65/TT_9DOF_!RESET: P45.P$1, P45.P$2, P45.P$3; also elsewhere on the board
AP4_GP66/TT_QI_TS_CTRL: P44.P$1, P44.P$2, P44.P$3; also elsewhere on the board
AP4_GP69/TT_FLASH_!CS: P42.P$1, P42.P$2, P42.P$3; also elsewhere on the board
AP4_GP72: P39.P$1, P39.P$2, P39.P$3; also elsewhere on the board
AP4_GP79: P22.P$1, P22.P$2, P22.P$3; also elsewhere on the board
AP4_GP80/SWTRACE0: J2.2 (SWDIO), J2.B2 (SWDIO); also elsewhere on the board
AP4_GP81/SWTRACE1: J2.4 (SWDCLK), J2.B4 (SWDCLK); also elsewhere on the board
AP4_GP82/SWTRACE2: J2.6 (SWO), J2.B6 (SWO), P18.P$1, P18.P$2, P18.P$3; also elsewhere on the board
AP4_GP83/SWTRACE3: J2.3 (!RESET), J2.B3 (!RESET), P19.P$1, P19.P$2, P19.P$3; also elsewhere on the board
AP4_GP88: P32.P$1, P32.P$2, P32.P$3; also elsewhere on the board
AP4_LED2_BLUE_COMM: D2.C1, R2.1
AP4_LED_RED_COMM: D2.C2, R1.1
AP4_SWDCLK: J1.4 (SWDCLK), J1.B4 (SWDCLK); also elsewhere on the board
AP4_SWDIO: J1.2 (SWDIO), J1.B2 (SWDIO); also elsewhere on the board
AP4_SWO: J1.6 (SWO), J1.B6 (SWO); also elsewhere on the board
AP4_SWTRACECLK: J2.1 (VTREF), J2.B1 (VTREF); also elsewhere on the board
AP4_USB0_N: P21.P$1, P21.P$2, P21.P$3; also elsewhere on the board
AP4_USB0_P: P20.P$1, P20.P$2, P20.P$3; also elsewhere on the board
AP4_VDDMIPI_1P8: P28.P$1, P28.P$2, P28.P$3, RZ4.1; also elsewhere on the board
AP4_VDDUSB_0P9: P26.P$1, P26.P$2, P26.P$3, RZ2.1; also elsewhere on the board
AP4_VDDUSB_3P3: P27.P$1, P27.P$2, P27.P$3, RZ3.1; also elsewhere on the board
BLE_RFOUT: P15.P$1, P15.P$2, P15.P$3; also elsewhere on the board
GND: C5.P$2 (2), C6.P$2 (2), J1.5 (GND), J1.B5 (GND), J2.5 (GND), J2.B5 (GND), P13.P$1, P13.P$2, P13.P$3, P37.P$1, P37.P$2, P37.P$3, RZ2.2, RZ3.2, RZ4.2, SJ1.1, VR2.2 (GND), VR2.PAD (GND); also elsewhere on the board
VDD: C5.P$1 (1), P29.P$1, P29.P$2, P29.P$3, RZ5.1, VR2.4 (IN)
VDDAUDA_1P8-CLEAN: RZ6.2; also elsewhere on the board
VR2_EN: RZ5.2, VR2.3 (EN)
VR2_OUT: C6.P$1 (1), RZ6.1, VR2.1 (OUT)

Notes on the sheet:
Ambiq Eng Note— VDDAUDA must be powered (even if not using BLE or AUDADC). I see you have an enable triggered by a pin. Note this can cause issues.
datasheet est's Rdrp =Ω If tgt: 20 mA ~~dissp 10mW~~ Vf red: 1.5 0.3V 15Ω 6mW Vf grn: 1.7 0.1V 5Ω 2mW Vf blu: 1.7 0.1V 5Ω 2mW

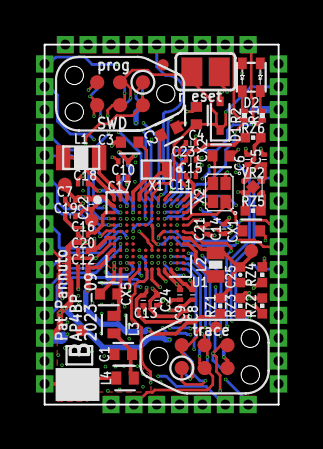
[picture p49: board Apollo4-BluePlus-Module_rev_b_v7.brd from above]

Board: 4 copper layers, 13.0 x 20.0 mm, 101 parts (0 on the bottom side), 73 nets.

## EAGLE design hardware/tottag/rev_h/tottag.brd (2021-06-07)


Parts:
A4: AMCA72-2R47G-S1F-T; AMCA72-2R470G-S1F-T
C1: 0.5pF; 0402_CAP; MPN GJM1555C1HR50WB01D; DIGIKEY 490-11250-1-ND
C2: 0.8pF; 0402_CAP; MPN GJM1555C1HR80WB01D; DIGIKEY 490-11253-1-ND
C8, C9, C10, C11: 12pF; 0402_CAP; MPN CBR04C120F5GAC; DIGIKEY 399-8815-2-ND
C18: 47pF; 0402_CAP; MPN GRM1555C1H470JA01D; DIGIKEY 490-5942-1-ND
C19: 100pF; 0402_CAP; MPN GRM1555C1H101JA01D; DIGIKEY 490-5922-1-ND
C24: 820pF; 0402_CAP; MPN C0402C821J5GACTU; DIGIKEY 399-11129-2-ND
C36: 47nF; 0402_CAP; MPN C1005X7R1C473K050BC; DIGIKEY 445-1264-1-ND
C39, C40, C41: 0.1uF; 0402_CAP; MPN GRM155R71C104KA88J; DIGIKEY 490-6328-1-ND
C42: 0.1uF; 0402_CAP
C71: 1uF; 0402_CAP
C72, C74, C76: 1uF; 0402_CAP; MPN GRM155R70G105KA12D; DIGIKEY 490-7195-1-ND
C83: 4.7uF; 0402_CAP
C89, C90: 4.7uF; 0402_CAP; MPN C1005X5R0J475K050BC; DIGIKEY 445-5947-1-ND
D2: SML-LX0404SIUPGUSB; 1MM_SQ_4PAD
D4: DIODE0402; 0402_DIODE; MPN CDSQR400B-HF; DIGIKEY 641-2087-1-ND
J3: TC2030-JLINK-NL-2SIDE; TC2030-IDC-NL-2SIDE
L1: 4.7nH; 0402_CAP; MPN LQW15AN4N7G8ZD; DIGIKEY 490-15482-1-ND
L2: 15nH; 0402_CAP; MPN HK100515NJ-T; DIGIKEY 587-1521-1-ND
L3: 10uH; 0603_CAP; MPN LQM18FN100M00D; DIGIKEY 490-4025-1-ND
LS1: PUI_SMT-0440-T-2-R; SMT-0440-T-2-R
Q2: CSD75207W15; DSBGA
R1: 4.7; 0402_RES; MPN RMCF0402FT4R70; DIGIKEY RMCF0402FT4R70CT-ND
R8: 1k; 0402_RES; MPN RMCF0402FT1K00; DIGIKEY RMCF0402FT1K00CT-ND
R9, R10: 1k; 0402_RES
R20: 10k; 0402_RES; MPN RC0402JR-0710KL; DIGIKEY 311-10KJRCT-ND
R36: 100k; 0402_RES
TP1, TP2, TP3, TP4, TP15: TPTP06SQ; TP06SQ
TP13, TP16, TP17, TP18, TP19, TP20, TP21, TP22, TP23, TP24, TP25, TP26, TP27: TEST-POINT; PAD.03X.03
U7: NRF52840; AQFN73
U11: AB1815-T3; QFN-16-3MM
X1: 32.768kHz; ABS05
X3: 32MHz; TXC-7V
X5: ABS07-32.768KHZ-7-T; ABS07

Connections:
!CHG: U7.W24 (P1.02*); also elsewhere on the board
!NRF_CS_IMU: TP22.P$1, U7.AC11 (P0.16); also elsewhere on the board
!NRF_CS_RTC: R36.2, TP27.P$1, U7.A10 (P0.29*/AIN5), U11.12 (!CS)
!NRF_CS_SD: TP26.P$1, U7.AD8 (P0.13); also elsewhere on the board
!NRF_RST: J3.3 (!RESET), J3.B3 (!RESET), U7.AC13 (P0.18)
!PG: U7.V23 (P1.03*); also elsewhere on the board
!RTC_IRQ: U7.A12 (P0.02*/AIN0), U11.11 (FOUT/!IRQ1)
!SD_DETECT: U7.T2 (P0.11); also elsewhere on the board
+3V3: C39.1, C41.1, C42.1, C71.1, C74.1, C76.1, C83.1, D2.1 (VDD), D4.CATHODE, J3.1 (VCC), J3.B1 (VCC), LS1.+, R36.1, TP15.TP, U7.A20 (P1.10*), U7.A22 (VDD), U7.AD14 (VDD), U7.AD23 (VDD), U7.B1 (VDD), U7.W1 (VDD), U7.Y2 (VDDH), U11.13 (VCC); also elsewhere on the board
BATIN: U7.J1 (P0.04/AIN2); also elsewhere on the board
BLE_ANT: A4.S1, C1.1, L1.1
BUZZER_GATE: Q2.A1 (G1), Q2.C1 (G2), U7.A14 (P1.15*)
D+: U7.AD6 (D+); also elsewhere on the board
D-: U7.AD4 (D-); also elsewhere on the board
EXT_I2C_SCL: TP1.TP, U7.R1 (P1.09); also elsewhere on the board
EXT_I2C_SDA: TP2.TP, U7.U1 (P0.12); also elsewhere on the board
GND: C1.2, C2.2, C8.1, C9.1, C10.1, C11.1, C18.2, C19.2, C24.2, C36.2, C39.2, C40.2, C41.2, C42.2, C71.2, C72.2, C74.2, C76.2, C83.2, C89.2, C90.2, J3.5 (GND), J3.B5 (GND), Q2.A2 (D1), Q2.A3 (D1), Q2.B2 (D2), Q2.B3 (D1), Q2.C2 (D2), Q2.C3 (D2), R20.2, TP4.TP, U7.B7 (VSS), U7.B17 (P1.12*), U7.B19 (P1.11*), U7.F23 (VSS_PA), U7.GND (VSS), U11.3 (!EXTR), U11.10 (EXTI), U11.GND (VSS), X3.2 (GND), X3.4 (GND); also elsewhere on the board
LED_NRF_BLUE: R10.2, U7.P23 (P1.07*)
LED_NRF_BLUE_COMM: D2.3 (B), R10.1, TP18.P$1
LED_NRF_GREEN: R9.2, U7.T23 (P1.05*)
LED_NRF_GREEN_COMM: D2.4 (G), R9.1, TP17.P$1
LED_NRF_RED: R8.2, U7.U24 (P1.04*)
LED_NRF_RED_COMM: D2.2 (R), R8.1, TP16.P$1
MAG_DRDY: U7.AD22 (P1.00); also elsewhere on the board
MAG_INT: U7.AC19 (P0.23); also elsewhere on the board
unnamed: D4.ANODE, LS1.- (N), Q2.B1 (S)
unnamed: C2.1, L1.2, U7.H23 (ANT)
unnamed: C8.2, U7.B24 (XC1), X3.3 (2)
unnamed: C9.2, U7.A23 (XC2), X3.1
unnamed: C18.1, U11.14 (AF)
unnamed: L2.2, L3.1
unnamed: U11.16 (XI), X5.1
unnamed: U11.15 (XO), X5.2
NRF_DCC: L3.2, U7.B3 (DCC)
NRF_DECAP1: C40.1, U7.C1 (DEC1)
NRF_DECAP3: C19.1, U7.D23 (DEC3)
NRF_DECAP5: C24.1, U7.N24 (DEC5)
NRF_DECAP46: C36.1, C72.1, L2.1, U7.B5 (DEC4), U7.E24 (DEC6)
NRF_DECUSB: C89.1, U7.AC5 (DECUSB)
NRF_GPIO_0: TP13.P$1, U7.H2 (P0.27)
NRF_IMU_INT1: U7.AD12 (P0.17); also elsewhere on the board
NRF_IMU_INT2: U7.AD10 (P0.15); also elsewhere on the board
NRF_SPI0_MISO: TP21.P$1, U7.AD20 (P0.24); also elsewhere on the board
NRF_SPI0_MOSI: TP20.P$1, U7.AD18 (P0.22); also elsewhere on the board
NRF_SPI0_SCLK: TP19.P$1, U7.AD16 (P0.20); also elsewhere on the board
NRF_SPI2_MISO: TP25.P$1, U7.K2 (P0.05/AIN3), U11.6 (SDO); also elsewhere on the board
NRF_SPI2_MOSI: TP24.P$1, U7.M2 (P0.07), U11.9 (SDI); also elsewhere on the board
NRF_SPI2_SCLK: TP23.P$1, U7.L1 (P0.06), U11.7 (SCL); also elsewhere on the board
NRF_SWDCLK: J3.4 (SWDCLK), J3.B4 (SWDCLK), U7.AA24 (SWDCLK)
NRF_SWDIO: J3.2 (SWDIO), J3.B2 (SWDIO), U7.AC24 (SWDIO)
QI_TS_CTRL: U7.AC21 (P0.25); also elsewhere on the board
RTC_WDI: R20.1, U7.A8 (P0.31*/AIN7), U11.2 (WDI)
SD_EN: U7.AC9 (P0.14); also elsewhere on the board
STM_INTERRUPT: TP3.TP, U7.N1 (P0.08); also elsewhere on the board
STM_WKUP1: U7.G1 (P0.26); also elsewhere on the board
VBAT_RTC: U11.5 (VBAT); also elsewhere on the board
VUSB: R1.1; also elsewhere on the board
VUSB_NRF: C90.1, R1.2, U7.AD2 (VBUS)
XL3: C11.2, U7.D2 (P0.00/XL1), X1.A (1)
XL4: C10.2, U7.F2 (P0.01/XL2), X1.B (2)

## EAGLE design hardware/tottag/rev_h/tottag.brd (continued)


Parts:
A1, A2, A3: TAIYO-YUDEN-AH086M
B1: MS518SE; MS518SE-FL35E
C22, C23: 470pF; 0402_CAP; MPN GRM1555C1H471JA01J; DIGIKEY 490-6242-1-ND
C26: 10nF; 0402_CAP
C29, C30: 10nF; 0402_CAP; MPN GRM155R71H103KA88J; DIGIKEY 490-6351-2-ND
C31, C32, C33: 22nF; 0402_CAP; MPN GRM155R71E223JA61D; DIGIKEY 490-10699-2-ND
C34, C35: 22nF; 0402_CAP; MPN CC0402ZRY5V8BB223; DIGIKEY 311-3823-1-ND
C37: 0.1uF; 0402_CAP
C63, C64, C65: 0.1uF; 0402_CAP; MPN GRM155R71C104KA88J; DIGIKEY 490-6328-1-ND
C69, C70: 470nF; 0402_CAP; MPN GRT155R61E474ME01D; DIGIKEY 490-12270-1-ND
C75: 1uF; 0402_CAP
C77, C78: 1uF; 0402_CAP; MPN GRM155R70G105KA12D; DIGIKEY 490-7195-1-ND
C80, C81: 4.7uF; 0402_CAP
C92, C93, C94: 10uF; 0603_CAP; MPN CM105X5R106M25AT; DIGIKEY 1253-CM105X5R106M25ATCT-ND
D1: GREEN; LED-0603; MPN LTST-C191KGKT; DIGIKEY 160-1446-1-ND
J1: USB4110-GF-A; GCT_USB4110-GF-A
J5: MOLEX-PICO-SPOX-3SIDE; MOLEX-PICO-SPOX-3_SIDE
J6, J7, J8: PINHD-1X1; 1X01
JP2, JP3: JUMPER-SMT_3_1-NC_TRACE_SILK; SMT-JUMPER_3_1-NC_TRACE_SILK
L4: WURTH_COIL_760308103204
Q1: CSD75207W15; DSBGA
R2, R3: 97.6; 0402_RES; MPN RMCF0402FT97R6; DIGIKEY RMCF0402FT97R6CT-ND
R4, R5: 162; 0402_RES; MPN RMCF0402FT162R; DIGIKEY RMCF0402FT162RCT-ND
R7, R14, R15: 1k; 0402_RES
R16: 1.41k; 0402_RES; MPN RMCF0402FT1K40; DIGIKEY RMCF0402FT1K40CT-ND
R17: 2.2k; 0402_RES; MPN RMCF0402JT2K20; DIGIKEY RMCF0402JT2K20CT-ND
R18, R19: 5.1k; 0402_RES; MPN RMCF0402FT5K10; DIGIKEY RMCF0402FT5K10CT-ND
R21, R22, R23, R24: 10k; 0402_RES; MPN RC0402JR-0710KL; DIGIKEY 311-10KJRCT-ND
R37: 3.3M; 0402_RES; MPN RMCF0402FT3M30; DIGIKEY RMCF0402FT3M30CT-ND
R38: 10M; 0402_RES; MPN RMCF0402FT10M0; DIGIKEY RMCF0402FT10M0CT-ND
R39: DNP; 0402_RES
RT1: 10k@25C; 0402_RES; MPN NCU15XH103F60RC; DIGIKEY 490-18149-1-ND
S1: 450404015514; DIGIKEY 732-13665-1-ND
U2: BQ24040; DSQ0010A
U5: MAX8887EZK33+T; SOT-23-5
U6: BQ51013B; RHL0020A

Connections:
!AD_EN: Q1.A1 (G1), Q1.C1 (G2), U6.8 (!AD-EN)
!CHG: D1.C, U2.8 (!CHG), U6.7 (!CHG); also elsewhere on the board
!PG: U2.5 (!PG); also elsewhere on the board
+3V3: C81.1, R7.1, U5.5 (OUT); also elsewhere on the board
BATIN: C37.2, R37.1, R38.2; also elsewhere on the board
BATT_THERM: J5.2, J5.2SUPP (2), J7.1, JP2.3
BATT_TS: JP2.2, U2.9 (TS)
BQ_AC1: C22.1, C23.1, C29.2, C31.1, C32.1, C33.1, C34.2, C69.2, U6.2 (AC1)
BQ_AC2: C22.2, C23.2, C30.2, C35.2, C70.2, L4.P$2 (2), U6.19 (AC2)
BQ_BOOT1: C29.1, U6.3 (BOOT1)
BQ_BOOT2: C30.1, U6.17 (BOOT2)
BQ_CLAMP1: C69.1, U6.5 (CLAMP1)
BQ_CLAMP2: C70.1, U6.16 (CLAMP2)
BQ_COMM1: C34.1, U6.6 (COMM1)
BQ_COMM2: C35.1, U6.15 (COMM2)
BQ_FOD: R3.1, R5.2, R23.2, U6.14 (FOD)
BQ_ILM: R4.1, U6.12 (ILIM)
BQ_RECT: C63.1, C92.1, C93.1, R22.1, U6.18 (RECT)
COIL_AC1: C31.2, C32.2, C33.2, L4.P$1 (1)
D+: J1.A6 (DP1), J1.B6 (DP2); also elsewhere on the board
D-: J1.A7 (DN1), J1.B7 (DN2); also elsewhere on the board
GND: B1.-, C26.2, C37.1, C63.2, C64.2, C65.2, C75.1, C77.2, C78.2, C80.2, C81.2, C92.2, C93.2, C94.2, J1.A1/B12 (GND), J1.B1/A12 (GND), J1.S1 (GND), J1.S2 (GND), J1.S3 (GND), J1.S4 (GND), J5.1, J5.1SUPP (1), J8.1, R2.2, R15.1, R17.1, R18.2, R19.2, R21.1, R24.1, R38.1, R39.1, U2.3 (VSS), U2.7 (ISET2), U2.PAD (VSS), U5.2 (GND), U6.1 (PGND), U6.10 (EN1), U6.11 (EN2), U6.20 (PGND), U6.PAD (PGND); also elsewhere on the board
unnamed: J1.B5 (CC2), R19.1
unnamed: C26.1, U5.4 (BP)
unnamed: J1.A5 (CC1), R18.1
unnamed: R2.1, R3.2
unnamed: R17.2, U2.2 (ISET)
unnamed: B1.+, R16.2
unnamed: JP2.1, R21.2
unnamed: R39.2, U2.4 (PRETERM)
unnamed: D1.A, R7.2
unnamed: R22.2, R23.1
unnamed: R4.2, R5.1
unnamed: JP3.1, R24.2
unnamed: JP3.3, RT1.2
unnamed: R14.2, RT1.1
unnamed: R14.1, R15.2
QI_TS_CTRL: C65.1, JP3.2, U6.13 (TS/CTRL); also elsewhere on the board
RF1: A1.A; also elsewhere on the board
RF2: A2.A; also elsewhere on the board
RF3: A3.A; also elsewhere on the board
VBAT: C78.1, J5.3, J5.3SUPP (3), J6.1, R37.2, S1.2, U2.10 (OUT)
VBAT_RTC: R16.1; also elsewhere on the board
VBAT_SWITCHED: C80.1, S1.1, U5.1 (IN), U5.3 (!SHDN)
VQI: C64.1, C77.1, C94.1, Q1.A2 (D1), Q1.A3 (D1), Q1.B3 (D1), U2.1 (IN), U6.4 (OUT)
VUSB: C75.2, J1.A4/B9 (VBUS), J1.B4/A9 (VBUS), Q1.B2 (D2), Q1.C2 (D2), Q1.C3 (D2), U6.9 (AD); also elsewhere on the board


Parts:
C38, C66, C67, C68: 0.1uF; 0402_CAP; MPN GRM155R71C104KA88J; DIGIKEY 490-6328-1-ND
C79: 1uF; 0402_CAP; MPN GRM155R70G105KA12D; DIGIKEY 490-7195-1-ND
C82: 4.7uF; 0402_CAP; MPN C1005X5R0J475K050BC; DIGIKEY 445-5947-1-ND
J2: DM3AT-SF-PEJM5
JP4: JUMPER-SMT_2_NC_TRACE_SILK; SMT-JUMPER_2_NC_TRACE_SILK
R25, R26: 10k; 0402_RES; MPN RC0402JR-0710KL; DIGIKEY 311-10KJRCT-ND
R30, R31, R32, R33, R34: 100k; 0402_RES
TP28, TP29: TEST-POINT; PAD.03X.03
U3: LSM6DSOXTR; LGA-14L_STM
U8: SIP32510; TSOT23-6
U12: LIS3MDL; LGA-12

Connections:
!NRF_CS_IMU: U3.12 (CS); also elsewhere on the board
!NRF_CS_SD: J2.2 (DATA3-CD/CS_N), R33.1; also elsewhere on the board
!SD_DETECT: J2.A, R31.1; also elsewhere on the board
+3V3: C38.2, C66.1, C68.1, C79.1, R25.1, R26.1, U3.5 (VDDIO), U3.8 (VDD), U8.5 (VSUPP), U8.6 (VSUPP), U12.5 (VDD), U12.6 (VDD_IO), U12.10 (CS); also elsewhere on the board
GND: C38.1, C66.2, C67.2, C68.2, C79.2, C82.2, J2.6 (GND), J2.B, J2.MOUNT0 (GND), J2.MOUNT1 (GND), J2.MOUNT2 (GND), J2.MOUNT3 (GND), R30.2, U3.6 (GND_2), U3.7 (GND), U8.4 (GND), U12.2 (GND), U12.3 (GND), U12.9 (SDO/SA1), U12.12 (GND); also elsewhere on the board
LSM_SENSEHUB_SCL: R26.2, TP28.P$1, U3.3 (SCX), U12.1 (SCL/SPC)
LSM_SENSEHUB_SDA: R25.2, TP29.P$1, U3.2 (SDX), U12.11 (SDA/SDI/SDO)
MAG_DRDY: JP4.1, U12.8 (DRDY); also elsewhere on the board
MAG_INT: U12.7 (INT); also elsewhere on the board
unnamed: C67.1, U12.4 (C1)
NRF_IMU_INT1: U3.4 (INT1); also elsewhere on the board
NRF_IMU_INT2: JP4.2, U3.9 (INT2); also elsewhere on the board
NRF_SPI0_MISO: U3.1 (SDO/SA0); also elsewhere on the board
NRF_SPI0_MOSI: U3.14 (SDA); also elsewhere on the board
NRF_SPI0_SCLK: U3.13 (SCL); also elsewhere on the board
NRF_SPI2_MISO: J2.7 (DATA0/MISO), R34.1; also elsewhere on the board
NRF_SPI2_MOSI: J2.3 (CMD/MOSI), R32.1; also elsewhere on the board
NRF_SPI2_SCLK: J2.5 (CLK); also elsewhere on the board
SD_EN: R30.1, U8.3 (EN); also elsewhere on the board
VCC_SDCARD: C82.1, J2.4 (VCC), R31.2, R32.2, R33.2, R34.2, U8.1 (VLOAD), U8.2 (VLOAD)


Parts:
+1V8: TPTP06SQ; TP06SQ
C3: 1.2pF; 0402_CAP; MPN GJM1555C1H1R2CB01D; DIGIKEY 490-3085-1-ND
C4, C5: 10pF; 0402_CAP; MPN 885012005074; DIGIKEY 732-12054-1-ND
C6, C7: 12pF; 0201_CAP; MPN CBR02C120F3GAC; DIGIKEY 399-8604-2-ND
C12, C13, C14, C15: 12pF; 0402_CAP; MPN CBR04C120F5GAC; DIGIKEY 399-8815-2-ND
C16: 18pF; 0402_CAP; MPN CBR04C180F5GAC; DIGIKEY 399-8828-1-ND
C17: 27pF; 0402_CAP; MPN GJM1555C1H270FB01D; DIGIKEY 490-16380-1-ND
C20, C21: 330pF; 0402_CAP; MPN CC0402JRX7R9BB331; DIGIKEY 311-3768-1-ND
C25: 820pF; 0402_CAP; MPN C0402C821J5GACTU; DIGIKEY 399-11129-2-ND
C27, C28: 10nF; 0402_CAP
C43, C44, C45, C46, C47, C48, C49, C50, C51, C52, C53, C54, C55, C56, C57, C58, C59, C60, C61, C62: 0.1uF; 0402_CAP
C73: 1uF; 0402_CAP
C84, C85, C86, C87, C88: 4.7uF; 0402_CAP
C91: 10uF; 0603_CAP; MPN CM105X5R106M25AT; DIGIKEY 1253-CM105X5R106M25ATCT-ND
C95: 47uF; 0603_CAP; MPN GRM188R60J476ME15D; DIGIKEY 490-13247-1-ND
D3: SML-LX0404SIUPGUSB; 1MM_SQ_4PAD
DW_SPI_CS: TPTP06SQ; TP06SQ
GP0, GP1: TEST-POINT; PAD.03X.03
J4: TC2030-JLINK-NL-2SIDE; TC2030-IDC-NL-2SIDE
JP1: JUMPER-SMT_2_NO_SILK; SMT-JUMPER_2_NO_SILK
MISO: TPTP06SQ; TP06SQ
MOSI: TPTP06SQ; TP06SQ
R6: 270; 0402_RES; MPN RMCF0402FT270R; DIGIKEY RMCF0402FT270RCT-ND
R11, R12, R13: 1k; 0402_RES
R27, R28: 11k; 0402_RES; MPN RMCF0402FT11K0; DIGIKEY RMCF0402FT11K0CT-ND
R29: 16k; 0402_RES; MPN RMCF0402FT16K0; DIGIKEY RMCF0402FT16K0CT-ND
R35: 100k; 0402_RES
SPI_CLK: TPTP06SQ; TP06SQ
T1: HHM1595A1; EIA-0805
TP5, TP6, TP10, TP11, TP12: TEST-POINT; PAD.03X.03
U1: DW1000; QFN-48-DW1000
U4: 1.8V; XCL20X
U9: SKY13317; MLPQ-UT-8
U10: STM32F091CC; UFQFPN-48
X2: 16MHz; FA-20H; MPN FA-20H 16.0000MF10Z-AJ3; DIGIKEY SER3913CT-ND
X4: 38.4MHz; FA-20H; MPN FA-20H 38.4000MF10Z-AS3; DIGIKEY SER3631CT-ND

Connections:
!DW_RST: U1.27 (!RST), U10.18 (PB0)
!DW_SPI_CS: DW_SPI_CS.TP, U1.24 (!SPICS), U10.14 (PA4)
!STM_RST: J4.3 (!RESET), J4.B3 (!RESET), U10.7 (!RST)
+1V8: +1V8.TP, C43.1, C46.1, C84.1, C91.1, JP1.2, U1.26 (VDDLDOD), U1.48 (VDDLDOA), U4.3 (VOUT), U4.8 (L2)
+3V3: C4.1, C5.1, C20.1, C21.1, C27.1, C28.1, C53.1, C54.1, C55.1, C56.1, C57.1, C58.1, C59.1, C60.1, C61.1, C73.1, C85.1, C86.1, C87.1, C88.1, C95.1, D3.1 (VDD), J4.1 (VCC), J4.B1 (VCC), JP1.1, U1.15 (VDDLNA), U1.18 (VDDPA1), U1.19 (VDDPA2), U1.25 (VDDAON), U1.28 (VDDIOA), U1.47 (VDDBAT), U4.6 (VIN), U10.1 (VBAT), U10.9 (VDDA), U10.24 (VDD/24), U10.36 (VDDIO2), U10.48 (VDD/48); also elsewhere on the board
ANT_SEL1: U9.3 (V1), U10.27 (PB14)
ANT_SEL2: U9.6 (V2), U10.26 (PB13)
ANT_SEL3: U9.7 (V3), U10.25 (PB12)
DW_IRQ: R35.2, U1.45 (IRQ/GPIO8), U10.20 (PB2)
DW_SPI_CLK: SPI_CLK.TP, U1.41 (SPICLK), U10.15 (PA5)
DW_SPI_MISO: MISO.TP, U1.40 (SPIMISO), U10.16 (PA6)
DW_SPI_MOSI: MOSI.TP, U1.39 (SPIMOSI), U10.17 (PA7)
DW_SYNC: U1.29 (SYNC/GPIO7)
DW_WAKEUP: U1.23 (WAKEUP), U10.19 (PB1)
EXT_I2C_SCL: U10.30 (PA9); also elsewhere on the board
EXT_I2C_SDA: U10.31 (PA10); also elsewhere on the board
GND: C4.2, C5.2, C12.2, C13.2, C14.2, C15.2, C20.2, C21.2, C27.2, C28.2, C43.2, C44.2, C45.2, C46.2, C47.2, C48.2, C49.2, C50.2, C51.2, C52.2, C53.2, C54.2, C55.2, C56.2, C57.2, C58.2, C59.2, C60.2, C61.2, C62.2, C73.2, C84.2, C85.2, C86.2, C87.2, C88.2, C91.2, C95.2, J4.5 (GND), J4.B5 (GND), R27.1, R28.2, R35.1, T1.2 (GND), T1.5 (GND), TP10.P$1, U1.22 (FORCEON), U1.32 (VSSIO/32), U1.43 (VSSIO/43), U1.46 (TESTMODE), U1.GND, U4.2 (GND), U4.5 (GND), U9.GND, U10.8 (VSSA), U10.23 (VSS/23), U10.35 (VSS/35), U10.47 (VSS/47), U10.GND, X2.2 (GND), X2.4 (GND), X4.2 (GND), X4.4 (GND); also elsewhere on the board
GPIO0: GP0.P$1, U10.42 (PB6)
GPIO1: GP1.P$1, U10.43 (PB7)
GPIO2: TP5.P$1, U10.29 (PA8)
GPIO3: TP6.P$1, U10.28 (PB15)
unnamed: T1.1 (UNB), U9.1 (RFC)
unnamed: C6.P$2 (2), T1.3 (BAL/3)
unnamed: C7.P$2 (2), T1.4 (BAL/4)
unnamed: C25.1, R6.2
unnamed: C17.1, R29.2
unnamed: C16.1, R6.1, U1.12 (VCOTUNE)
unnamed: C3.1, R29.1, U1.8 (CLKTUNE)
unnamed: R27.2, U1.5 (VREF)
unnamed: R28.1, U10.44 (PF11-BOOT0)
unnamed: TP11.P$1, U1.36 (GPIO2)
unnamed: TP12.P$1, U1.35 (GPIO3)
unnamed: U4.1 (LX), U4.7 (L1)
OSC_IN: C14.1, U10.5 (PF0-OSC_IN), X2.1
OSC_OUT: C15.1, U10.6 (PF1-OSC_OUT), X2.3 (2)
REG_EN: U1.21 (EXTON), U4.4 (CE/MODE)
RF1: U9.4 (RF1); also elsewhere on the board
RF2: U9.5 (RF2); also elsewhere on the board
RF3: U9.8 (RF3); also elsewhere on the board
RF_N: C6.P$1 (1), U1.17 (RF_N)
RF_P: C7.P$1 (1), U1.16 (RF_P)
STM_INTERRUPT: U10.12 (PA2); also elsewhere on the board
STM_LED_BLUE: R13.2, U10.40 (PB4)
STM_LED_BLUE_COMM: D3.3 (B), R13.1
STM_LED_GREEN: R12.2, U10.41 (PB5)
STM_LED_GREEN_COMM: D3.4 (G), R12.1
STM_LED_RED: R11.2, U10.39 (PB3)
STM_LED_RED_COMM: D3.2 (R), R11.1
STM_SWDCLK: J4.4 (SWDCLK), J4.B4 (SWDCLK), U10.37 (PA14)
STM_SWDIO: J4.2 (SWDIO), J4.B2 (SWDIO), U10.34 (PA13)
STM_WKUP1: U10.10 (PA0); also elsewhere on the board
VDDCLK: C3.2, C17.2, C48.1, U1.9 (VDDCLK)
VDDDIG: C44.1, C45.1, U1.20 (VDDREG), U1.44 (VDDDIG)
VDDIF: C51.1, U1.7 (VDDIF)
VDDIO: C50.1, C62.1, U1.31 (VDDIO/31), U1.42 (VDDIO/42)
VDDMS: C47.1, U1.6 (VDDMS)
VDDSYN: C49.1, U1.10 (VDDSYN)
VDDVCO: C16.2, C25.2, C52.1, U1.11 (VDDVCO)
XTAL1: C13.1, U1.3 (XTAL1), X4.3 (2)
XTAL2: C12.1, U1.4 (XTAL2), X4.1

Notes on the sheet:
For regularator caps, please use B, X5R, and X7R grades in temperature characteristics



Board: 4 copper layers, 68.1 x 39.6 mm, 218 parts (26 on the bottom side), 150 nets.

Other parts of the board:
U$1: TOTTERNARY_300MIL
U$2: UCSD_TRIDENT_SOLID_100MIL
U$3: ETH_200MIL
U$4: UCB_CAL_100MIL

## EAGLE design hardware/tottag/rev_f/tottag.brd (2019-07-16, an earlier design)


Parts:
A4: ANT3216A063R2400A
C1, C2: 1pF; 0402_CAP; MPN GJM1555C1H1R0CB01D; DIGIKEY 490-3083-1-ND
C8, C9, C10, C11: 12pF; 0402_CAP; MPN GRM1555C1H120GA01D; DIGIKEY 490-6197-1-ND
C18: 47pF; 0402_CAP; MPN GRM1555C1H470JA01D; DIGIKEY 490-5942-1-ND
C19: 100pF; 0402_CAP; MPN GRM1555C1H101JA01D; DIGIKEY 490-5922-1-ND
C22: 820pF; 0402_CAP; MPN CL05C821JB5NFNC; DIGIKEY 1276-6989-1-ND
C27: 47nF; 0402_CAP; MPN C1005X7R1C473K050BC; DIGIKEY 445-1264-1-ND
C31, C32, C33: 0.1uF; 0402_CAP; MPN GRM155R71C104KA88J; DIGIKEY 490-6328-1-ND
C34: 0.1uF; 0402_CAP
C56: 1uF; 0402_CAP
C57, C59: 1uF; 0402_CAP; MPN GRM155R70G105KA12D; DIGIKEY 490-7195-1-ND
C63: 4.7uF; 0402_CAP
D2: SML-LX0404SIUPGUSB; 1MM_SQ_4PAD
J4: TC2030-JLINK-NL; TC2030-IDC-NL
L1: 3.9nH; 0402_CAP; MPN AISC-0402-3N9G-T; DIGIKEY AISC-0402-3N9G-TCT-ND
L2: 15nH; 0402_CAP; MPN HK100515NJ-T; DIGIKEY 587-1521-1-ND
L3: 10uH; 0603_CAP; MPN LQM18FN100M00D; DIGIKEY 490-4025-1-ND
R4, R5, R6: 470; 0402_RES
R16, R17, R18: 10k; 0402_RES; MPN RC0402JR-0710KL; DIGIKEY 311-10KJRCT-ND
TP1, TP2, TP3, TP4, TP15: TPTP06SQ; TP06SQ
TP13, TP14: TEST-POINT; PAD.03X.03
U7: NRF52840; AQFN73
U11: AB1815-T3; QFN-16-3MM
X1: 32.768kHz; ABS05
X3: 32MHz; TXC-7V
X5: ABS07-32.768KHZ-7-T; 2-SMD

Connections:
!FT_RST: U7.P2 (P1.08); also elsewhere on the board
!NRF_CS_IMU: U7.AC11 (P0.16); also elsewhere on the board
!NRF_CS_RTC: R18.1, U7.A10 (P0.29/AIN5), U11.12 (!CS)
!NRF_CS_SD: U7.AD16 (P0.20); also elsewhere on the board
!NRF_RST: J4.3 (!RESET), U7.AC13 (P0.18)
!RTC_IRQ: U7.A12 (P0.02/AIN0), U11.11 (FOUT/!IRQ1)
!SD_DETECT: U7.AD22 (P1.00); also elsewhere on the board
+3V3: C31.1, C33.1, C34.1, C56.1, C63.1, D2.1 (VDD), J4.1 (VCC), TP15.TP, U7.A22 (VDD), U7.AD14 (VDD), U7.AD23 (VDD), U7.B1 (VDD), U7.W1 (VDD), U7.Y2 (VDDH); also elsewhere on the board
BATIN: U7.B9 (P0.30/AIN6); also elsewhere on the board
DBG_RX: U7.M2 (P0.07); also elsewhere on the board
DBG_TX: U7.T2 (P0.11); also elsewhere on the board
EXT_I2C_SCL: TP1.TP, U7.R1 (P1.09); also elsewhere on the board
EXT_I2C_SDA: TP2.TP, U7.U1 (P0.12); also elsewhere on the board
GND: A4.S2 (GND), C1.2, C2.2, C8.1, C9.1, C10.1, C11.1, C18.2, C19.2, C22.2, C27.2, C31.2, C32.2, C33.2, C34.2, C56.2, C57.2, C59.2, C63.2, J4.5 (GND), TP4.TP, U7.AD2 (VBUS), U7.B7 (VSS), U7.F23 (VSS_PA), U7.GND (VSS), U11.3 (!EXTR), U11.GND (VSS), X3.2 (GND), X3.4 (GND); also elsewhere on the board
LED_NRF_BLUE: R6.2, U7.J1 (P0.04/AIN2)
LED_NRF_GREEN: R5.2, U7.L1 (P0.06)
LED_NRF_RED: R4.2, U7.K2 (P0.05/AIN3)
unnamed: C22.1, U7.N24 (DEC5)
unnamed: C32.1, U7.C1 (DEC1)
unnamed: C27.1, C57.1, L2.1, U7.B5 (DEC4), U7.E24 (DEC6)
unnamed: C19.1, U7.D23 (DEC3)
unnamed: C1.1, L1.2, U7.H23 (ANT)
unnamed: A4.S1 (ANTENNA), C2.1, L1.1
unnamed: C8.2, U7.B24 (XC1), X3.3 (2)
unnamed: C9.2, U7.A23 (XC2), X3.1
unnamed: L3.2, U7.B3 (DCC)
unnamed: C18.1, U11.14 (AF)
unnamed: L2.2, L3.1
unnamed: U11.16 (XI), X5.1
unnamed: U11.15 (XO), X5.2
unnamed: R16.1, U11.10 (EXTI)
unnamed: D2.2 (R), R4.1
unnamed: D2.4 (G), R5.1
unnamed: D2.3 (B), R6.1
NRF_GPIO_0: TP13.P$1, U7.H2 (P0.27)
NRF_GPIO_1: TP14.P$1, U7.G1 (P0.26)
NRF_IMU_INT1: U7.AD18 (P0.22); also elsewhere on the board
NRF_IMU_INT2: U7.AD20 (P0.24); also elsewhere on the board
NRF_MISO: U7.AD10 (P0.15), U11.6 (SDO); also elsewhere on the board
NRF_MOSI: U7.AD8 (P0.13), U11.9 (SDI); also elsewhere on the board
NRF_SCK: U7.AD12 (P0.17), U11.7 (SCL); also elsewhere on the board
NRF_SWDCLK: J4.4 (SWDCLK), U7.AA24 (SWDCLK)
NRF_SWDIO: J4.2 (SWDIO), U7.AC24 (SWDIO)
RTC_WDI: R17.1, U7.A8 (P0.31/AIN7), U11.2 (WDI)
SD_EN: U7.AC9 (P0.14); also elsewhere on the board
STM_INTERRUPT: TP3.TP, U7.N1 (P0.08); also elsewhere on the board
VBAT_RTC: R16.2, R17.2, R18.2, U11.5 (VBAT); also elsewhere on the board
VCC: C59.1, U11.13 (VCC)
XL3: C11.2, U7.D2 (P0.00/XL1), X1.A (1)
XL4: C10.2, U7.F2 (P0.01/XL2), X1.B (2)

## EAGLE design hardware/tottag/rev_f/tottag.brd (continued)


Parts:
A1, A2, A3: TAIYO-YUDEN-AH086M
B1: MS518SE; MS518SE-FL35E
C24: 10nF; 0402_CAP
C28: 0.1uF; 0402_CAP
C29, C30: 0.1uF; 0402_CAP; MPN GRM155R71C104KA88J; DIGIKEY 490-6328-1-ND
C55: 1uF; 0402_CAP
C60, C61, C68, C69: 4.7uF; 0402_CAP
C62: 4.7uF; 0402_CAP; MPN C1005X5R0J475K050BC; DIGIKEY 445-5947-1-ND
C72: 10uF; 0603_CAP; MPN GRM188R60J106ME47D; DIGIKEY 490-3896-1-ND
D1: GREEN; LED-0603
J1: MICRO_USB_B_HIROSE_ZX62-B-5PA(11); USB_MICRO_B-HIROSE-ZX62-B-5PA(11)
J2: CON_MICRO_SDDM3AT-SF-PEJM5; DM3AT-SF-PEJM5
J3: BAT_HOLE; BATTERY_HOLE
R1, R2: 0; 0402_RES
R7: 1k; 0402_RES
R11: 1.41k; 0402_RES; MPN RC0402JR-0710KL; DIGIKEY 311-10KJRCT-ND
R12: 2k 1%; 0402_RES
R13, R14, R15: 10k; 0402_RES
R22, R23: 100k; 0402_RES
R25: 2.2M; 0402_RES
R26: 10M; 0402_RES
U2: FT232RQ; QFN32
U3: LIS2DW12; LGA-12
U5: MAX8887EZK33+T; SOT-23-5
U6: MCP73831; DFN-8-MCP
U8: SIP32510; TSOT23-6

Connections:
!CHRG: D1.A, R7.1
!FT_RST: U2.18 (!RESET); also elsewhere on the board
!NRF_CS_IMU: U3.2 (CS); also elsewhere on the board
!NRF_CS_SD: J2.2 (DATA3-CD/CS_N), R14.1; also elsewhere on the board
!SD_DETECT: J2.A, R23.1; also elsewhere on the board
+3V3: C30.1, C61.1, C72.1, U3.9 (VCC), U3.10 (VDD_IO), U5.5 (OUT), U8.5 (VSUPP), U8.6 (VSUPP); also elsewhere on the board
BATIN: C28.2, R25.2, R26.1; also elsewhere on the board
D+: J1.3 (D+), U2.14 (USBDP)
D-: J1.2 (D-), U2.15 (USBDM)
DBG_RX: R1.2; also elsewhere on the board
DBG_TX: R2.2; also elsewhere on the board
GND: B1.-, C24.2, C28.1, C29.2, C30.2, C55.2, C60.2, C61.2, C62.2, C68.2, C69.2, C72.2, J1.5 (GND), J2.6 (GND), J2.B, J2.MOUNT0 (GND), J2.MOUNT1 (GND), J2.MOUNT2 (GND), J2.MOUNT3 (GND), J3.N (-), R12.1, R22.2, R25.1, U2.4 (GND), U2.17 (GND), U2.20 (GND), U2.24 (GND), U2.26 (TEST), U3.5 (GND), U3.6 (GND), U3.7 (GND), U3.8 (GND), U5.2 (GND), U6.6 (VSS), U6.GND, U8.4 (GND); also elsewhere on the board
unnamed: C29.1, U2.1 (VCCIO), U2.16 (3V3OUT)
unnamed: D1.C, U6.5 (STAT)
unnamed: C24.1, U5.4 (BP)
unnamed: R12.2, U6.8 (PROG)
unnamed: R1.1, U2.30 (TXD)
unnamed: R2.1, U2.2 (RXD)
unnamed: B1.+, R11.2
unnamed: C62.1, J2.4 (VCC), R13.2, R14.2, R15.2, R23.2, U8.1 (VLOAD), U8.2 (VLOAD)
NRF_IMU_INT1: U3.12 (INT1); also elsewhere on the board
NRF_IMU_INT2: U3.11 (INT2); also elsewhere on the board
NRF_MISO: J2.7 (DATA0/MISO), R15.1, U3.3 (MISO/SA0); also elsewhere on the board
NRF_MOSI: J2.3 (CMD/MOSI), R13.1, U3.4 (MOSI/SDA); also elsewhere on the board
NRF_SCK: J2.5 (CLK), U3.1 (SCL/SPC); also elsewhere on the board
RF1: A1.A; also elsewhere on the board
RF2: A2.A; also elsewhere on the board
RF3: A3.A; also elsewhere on the board
SD_EN: R22.1, U8.3 (EN); also elsewhere on the board
VBAT: C60.1, C69.1, J3.P (+), R26.2, U5.1 (IN), U5.3 (!SHDN), U6.3 (VBAT/3), U6.4 (VBAT/4)
VBAT_RTC: R11.1; also elsewhere on the board
VUSB: C55.1, C68.1, J1.1 (+5V), R7.2, U2.19 (VCC), U6.1 (VDD/1), U6.2 (VDD/2)


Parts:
+1V8: TPTP06SQ; TP06SQ
C3: 1.2pF; 0402_CAP
C4, C5: 10pF; 0402_CAP
C6, C7: 12pF; 0201_CAP
C12, C13, C14, C15: 12pF; 0402_CAP
C16: 18pF; 0402_CAP
C17: 27pF; 0402_CAP
C20, C21: 330pF; 0402_CAP
C23: 820pF; 0402_CAP
C25, C26: 10nF; 0402_CAP
C35, C36, C37, C38, C39, C40, C41, C42, C43, C44, C45, C46, C47, C48, C49, C50, C51, C52, C53, C54: 0.1uF; 0402_CAP
C58: 1uF; 0402_CAP
C64, C65, C66, C67, C70: 4.7uF; 0402_CAP
C71: 10uF; 0402_CAP
C73: 47uF; 0603_CAP
D3: SML-LX0404SIUPGUSB; 1MM_SQ_4PAD
GPIO0, GPIO1: TEST-POINT; PAD.03X.03
J5: TC2030-JLINK-NL; TC2030-IDC-NL
JP1: JUMPER-SMT_2_NO_NO-SILK; SMT-JUMPER_2_NO_NO-SILK
MISO: TPTP06SQ; TP06SQ
MOSI: TPTP06SQ; TP06SQ
R3: 270; 0402_RES
R8, R9, R10: 1k; 0402_RES
R19: 11k 1%; 0402_RES
R20: 11k; 0402_RES
R21: 16k; 0402_RES
R24: 100k; 0402_RES
SPI_CLK: TPTP06SQ; TP06SQ
T1: HHM1595A1; EIA-0805
TP5, TP6, TP7, TP8, TP9, TP10, TP11, TP12: TEST-POINT; PAD.03X.03
U1: DW1000; QFN-48-DW1000
U4: XCL206B; XCL20X
U9: SKY13317; MLPQ-UT-8
U10: STM32F091CC; UFQFPN-48
X2: 16MHz; FA-20H; DIGIKEY SER3913CT-ND
X4: 38.4MHz; FA-20H; DIGIKEY SER3631CT-ND

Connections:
!DW_RST: U1.27 (!RST), U10.18 (PB0)
!DW_SPI_CS: U1.24 (!SPICS), U10.14 (PA4)
!STM_RST: J5.3 (!RESET), U10.7 (!RST)
+1V8: +1V8.TP, C35.1, C38.1, C64.1, C71.1, JP1.2, U1.26 (VDDLDOD), U1.48 (VDDLDOA), U4.3 (VOUT), U4.8 (L2)
+3V3: C4.1, C5.1, C20.1, C21.1, C25.1, C26.1, C45.1, C46.1, C47.1, C48.1, C49.1, C50.1, C51.1, C52.1, C53.1, C58.1, C65.1, C66.1, C67.1, C70.1, C73.1, D3.1 (VDD), J5.1 (VCC), JP1.1, U1.15 (VDDLNA), U1.18 (VDDPA1), U1.19 (VDDPA2), U1.25 (VDDAON), U1.28 (VDDIOA), U1.47 (VDDBAT), U4.6 (VIN), U10.1 (VBAT), U10.9 (VDDA), U10.24 (VDD/24), U10.36 (VDDIO2), U10.48 (VDD/48); also elsewhere on the board
ANT_SEL1: U9.3 (V1), U10.27 (PB14)
ANT_SEL2: U9.6 (V2), U10.26 (PB13)
ANT_SEL3: U9.7 (V3), U10.25 (PB12)
DW_IRQ: R24.2, U1.45 (IRQ/GPIO8), U10.20 (PB2)
DW_SPI_CLK: SPI_CLK.TP, U1.41 (SPICLK), U10.15 (PA5)
DW_SPI_MISO: MISO.TP, U1.40 (SPIMISO), U10.16 (PA6)
DW_SPI_MOSI: MOSI.TP, U1.39 (SPIMOSI), U10.17 (PA7)
DW_SYNC: U1.29 (SYNC/GPIO7)
DW_WAKEUP: U1.23 (WAKEUP), U10.19 (PB1)
EXT_I2C_SCL: U10.30 (PA9); also elsewhere on the board
EXT_I2C_SDA: U10.31 (PA10); also elsewhere on the board
GND: C4.2, C5.2, C12.2, C13.2, C14.2, C15.2, C20.2, C21.2, C25.2, C26.2, C35.2, C36.2, C37.2, C38.2, C39.2, C40.2, C41.2, C42.2, C43.2, C44.2, C45.2, C46.2, C47.2, C48.2, C49.2, C50.2, C51.2, C52.2, C53.2, C54.2, C58.2, C64.2, C65.2, C66.2, C67.2, C70.2, C71.2, C73.2, J5.5 (GND), R19.1, R20.2, R24.1, T1.2 (GND), T1.5 (GND), TP10.P$1, U1.22 (FORCEON), U1.32 (VSSIO/32), U1.43 (VSSIO/43), U1.46 (TESTMODE), U1.GND, U4.2 (GND), U4.5 (GND), U9.GND, U10.8 (VSSA), U10.23 (VSS/23), U10.35 (VSS/35), U10.47 (VSS/47), U10.GND, X2.2 (GND), X2.4 (GND), X4.2 (GND), X4.4 (GND); also elsewhere on the board
GPIO0: GPIO0.P$1, U10.42 (PB6)
GPIO1: GPIO1.P$1, U10.43 (PB7)
GPIO2: TP5.P$1, U10.29 (PA8)
GPIO3: TP6.P$1, U10.28 (PB15)
LED_BLUE: R10.2, U10.40 (PB4)
LED_GREEN: R9.2, U10.41 (PB5)
LED_RED: R8.2, U10.39 (PB3)
unnamed: T1.1 (UNB), U9.1 (RFC)
unnamed: C6.P$2 (2), T1.3 (BAL/3)
unnamed: C7.P$2 (2), T1.4 (BAL/4)
unnamed: C23.1, R3.2
unnamed: C17.1, R21.2
unnamed: C16.1, R3.1, U1.12 (VCOTUNE)
unnamed: C3.1, R21.1, U1.8 (CLKTUNE)
unnamed: R19.2, U1.5 (VREF)
unnamed: R20.1, U10.44 (PF11-BOOT0)
unnamed: D3.4 (G), R9.1, TP7.P$1
unnamed: D3.3 (B), R10.1, TP9.P$1
unnamed: D3.2 (R), R8.1, TP8.P$1
unnamed: TP11.P$1, U1.36 (GPIO2)
unnamed: TP12.P$1, U1.35 (GPIO3)
unnamed: U4.1 (LX), U4.7 (L1)
OSC_IN: C14.1, U10.5 (PF0-OSC_IN), X2.1
OSC_OUT: C15.1, U10.6 (PF1-OSC_OUT), X2.3 (2)
REG_EN: U1.21 (EXTON), U4.4 (CE/MODE)
RF1: U9.4 (RF1); also elsewhere on the board
RF2: U9.5 (RF2); also elsewhere on the board
RF3: U9.8 (RF3); also elsewhere on the board
RF_N: C6.P$1 (1), U1.17 (RF_N)
RF_P: C7.P$1 (1), U1.16 (RF_P)
STM_INTERRUPT: U10.12 (PA2); also elsewhere on the board
STM_SWCLK: J5.4 (SWDCLK), U10.37 (PA14)
STM_SWDIO: J5.2 (SWDIO), U10.34 (PA13)
VDDCLK: C3.2, C17.2, C40.1, U1.9 (VDDCLK)
VDDDIG: C36.1, C37.1, U1.20 (VDDREG), U1.44 (VDDDIG)
VDDIF: C43.1, U1.7 (VDDIF)
VDDIO: C42.1, C54.1, U1.31 (VDDIO/31), U1.42 (VDDIO/42)
VDDMS: C39.1, U1.6 (VDDMS)
VDDSYN: C41.1, U1.10 (VDDSYN)
VDDVCO: C16.2, C23.2, C44.1, U1.11 (VDDVCO)
XTAL1: C13.1, U1.3 (XTAL1), X4.3 (2)
XTAL2: C12.1, U1.4 (XTAL2), X4.1

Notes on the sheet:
For regularator caps, please use B, X5R, and X7R grades in temperature characteristics



Board: 4 copper layers, 61.0 x 34.5 mm, 157 parts (40 on the bottom side), 116 nets.

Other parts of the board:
U$1: TOTTERNARY_300MIL
U$3: ETH_200MIL
U$4: UCB_CAL_100MIL

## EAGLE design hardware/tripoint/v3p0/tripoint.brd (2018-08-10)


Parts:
C1, C2: 12pF; 0201_CAP
C3, C6, C37, C38, C43: 4.7uF; 0402_CAP
C4: 10uF; 0603_CAP
C5, C7, C8, C9, C10, C11, C12, C13, C14, C15, C21, C22, C23, C24, C25, C42: 0.1uF; 0402_CAP
C16, C17: 10pF; 0402_CAP
C18, C19: 330pF; 0402_CAP
C20: 0.01uF; 0402_CAP
C26: 820pF; 0402_CAP
C27: 27pF; 0402_CAP
C28: 1.2pF; 0402_CAP
C29: 18pF; 0402_CAP
C30, C31, C32, C33: 12pF; 0402_CAP
C34, C35, C36, C39: 100nF; 0402_CAP
C40: 1uF; 0402_CAP
C41: 10nF; 0402_CAP
D1: SML-LX0404SIUPGUSB; 1MM_SQ_4PAD
GPIO0, GPIO1: TEST_POINT_0.040IN; TESTPOINT_0.040IN
J2: TC2030-JLINK-NL; TC2030-IDC-NL
R1: 270; 0402_RES
R2: 16k; 0402_RES
R3: 11k 1%; 0402_RES
R4: 11k; 0402_RES
R5, R6, R7: 1k; 0402_RES
R8: 100k; 0402_RES
T1: HHM1595A1; EIA-0805
TP3, TP4, TP5, TP6, TP7, TP8, TP9, TP10: TEST-POINT; PAD.03X.03
U1: STM32F091CC; UFQFPN-48
U2: DW1000; QFN-48-DW1000
U3: SKY13317; MLPQ-UT-8
U4: LXDC2HN18A; LXDC2HN
X1: 38.4M; FA-20H; DIGIKEY SER3631CT-ND
X2: 16M; FA-20H; DIGIKEY SER3913CT-ND
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

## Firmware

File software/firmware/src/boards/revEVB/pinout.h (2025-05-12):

#ifndef __PINOUT_HEADER_H__
#define __PINOUT_HEADER_H__

// Hardware Revision ID
#include "revisions.h"
#define REVISION_ID                                 REVISION_APOLLO4_EVB

// Battery
#define PIN_BATTERY_VOLTAGE                         18
#define PIN_BATTERY_VOLTAGE_FUNCTION                AM_HAL_PIN_18_ADCSE1
#define PIN_BATTERY_VOLTAGE_ADC_CHANNEL             AM_HAL_ADC_SLOT_CHSEL_SE1
#define PIN_BATTERY_CHARGING_STATUS                 25
#define PIN_BATTERY_INPUT_POWER_GOOD                26
#define PIN_BATTERY_CHARGE_COMPLETE_SIGNAL          27
#define VOLTAGE_DIVIDER_LOWER                       33
#define VOLTAGE_DIVIDER_UPPER                       51

// Buttons
#define PIN_BUTTON_1                                AM_BSP_GPIO_BUTTON0
#define PIN_BUTTON_2                                AM_BSP_GPIO_BUTTON1

// Buzzer
#define PIN_BUZZER_DRIVER                           28

// DecaWave Radio
#define RADIO_SPI_NUMBER                            6
#define PIN_RADIO_SPI_SCK                           61
#define PIN_RADIO_SPI_MISO                          63
#define PIN_RADIO_SPI_MOSI                          62
#define PIN_RADIO_SPI_CS                            47
#define PIN_RADIO_INTERRUPT                         48
#define PIN_RADIO_RESET                             53
#define PIN_RADIO_WAKEUP                            49
#define PIN_RADIO_ANTENNA_SELECT1                   25
#define PIN_RADIO_ANTENNA_SELECT2                   26
#define PIN_RADIO_SPI_SCK_FUNCTION                  AM_HAL_PIN_61_M6SCK
#define PIN_RADIO_SPI_MISO_FUNCTION                 AM_HAL_PIN_63_M6MISO
#define PIN_RADIO_SPI_MOSI_FUNCTION                 AM_HAL_PIN_62_M6MOSI
#define PIN_RADIO_SPI_CS_FUNCTION                   AM_HAL_PIN_47_NCE47

// IMU
#define IMU_I2C_NUMBER                              0
#define IMU_I2C_ADDRESS                             0x29
#define PIN_IMU_I2C_SCL                             5
#define PIN_IMU_I2C_SDA                             6
#define PIN_IMU_I2C_SCL_FUNCTION                    AM_HAL_PIN_5_M0SCL
#define PIN_IMU_I2C_SDA_FUNCTION                    AM_HAL_PIN_6_M0SDAWIR3
#define PIN_IMU_INTERRUPT                           0
#define PIN_IMU_RESET                               0

// LEDs
#define PIN_LED1_RED                                AM_BSP_GPIO_LED0
#define PIN_LED1_GREEN                              AM_BSP_GPIO_LED1
#define PIN_LED2_RED                                AM_BSP_GPIO_LED0
#define PIN_LED2_YELLOW                             AM_BSP_GPIO_LED2

// Logging
#define PIN_SWO                                     28
#define PIN_SWO_FUNCTION                            AM_HAL_PIN_28_SWO

// Memory Storage (SPI)
#define STORAGE_SPI_NUMBER                          1
#define PIN_STORAGE_SPI_SCK                         8
#define PIN_STORAGE_SPI_MISO                        10
#define PIN_STORAGE_SPI_MOSI                        9
#define PIN_STORAGE_SPI_CS                          11
#define PIN_STORAGE_SPI_SCK_FUNCTION                AM_HAL_PIN_8_M1SCK
#define PIN_STORAGE_SPI_MISO_FUNCTION               AM_HAL_PIN_10_M1MISO
#define PIN_STORAGE_SPI_MOSI_FUNCTION               AM_HAL_PIN_9_M1MOSI
#define PIN_STORAGE_SPI_CS_FUNCTION                 AM_HAL_PIN_11_NCE11
#define PIN_STORAGE_WRITE_PROTECT                   12
#define PIN_STORAGE_HOLD                            13
#define MEMORY_PAGE_SIZE_BYTES                      2048
#define MEMORY_BLOCK_COUNT                          1024
#define MEMORY_ECC_BYTES_PER_PAGE                   64
#define STORAGE_DEVICE_ID                           { 0xEF, 0xBA, 0x21 }

// Timers
#define BUZZER_TIMER_NUMBER                         0
#define RADIO_WAKEUP_TIMER_NUMBER                   2
#define RADIO_WAKEUP_TIMER_TICK_RATE_HZ             (AM_HAL_CLKGEN_FREQ_MAX_HZ / 16)
#define BLE_SCANNING_TIMER_NUMBER                   3
#define BLE_SCANNING_TIMER_TICK_RATE_HZ             (AM_HAL_CLKGEN_FREQ_MAX_HZ / 16)

#endif  // #ifndef __PINOUT_HEADER_H__

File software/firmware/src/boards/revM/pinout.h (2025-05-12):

#ifndef __PINOUT_HEADER_H__
#define __PINOUT_HEADER_H__

// Hardware Revision ID
#include "revisions.h"
#define REVISION_ID                                 REVISION_M

// Battery
#define PIN_BATTERY_VOLTAGE                         18
#define PIN_BATTERY_VOLTAGE_FUNCTION                AM_HAL_PIN_18_ADCSE1
#define PIN_BATTERY_VOLTAGE_ADC_CHANNEL             AM_HAL_ADC_SLOT_CHSEL_SE1
#define PIN_BATTERY_CHARGING_STATUS                 58
#define PIN_BATTERY_INPUT_POWER_GOOD                60
#define PIN_BATTERY_CHARGE_COMPLETE_SIGNAL          66
#define VOLTAGE_DIVIDER_LOWER                       187
#define VOLTAGE_DIVIDER_UPPER                       510

// Buzzer
#define PIN_BUZZER_DRIVER                           55

// DecaWave Radio
#define RADIO_SPI_NUMBER                            3
#define PIN_RADIO_SPI_SCK                           31
#define PIN_RADIO_SPI_MISO                          33
#define PIN_RADIO_SPI_MOSI                          32
#define PIN_RADIO_SPI_CS                            24
#define PIN_RADIO_SPI_CS2                           29
#define PIN_RADIO_SPI_CS3                           25
#define PIN_RADIO_INTERRUPT                         72
#define PIN_RADIO_INTERRUPT2                        27
#define PIN_RADIO_INTERRUPT3                        76
#define PIN_RADIO_RESET                             82
#define PIN_RADIO_RESET2                            50
#define PIN_RADIO_RESET3                            83
#define PIN_RADIO_WAKEUP                            63
#define PIN_RADIO_WAKEUP2                           26
#define PIN_RADIO_WAKEUP3                           88
#define PIN_RADIO_SPI_SCK_FUNCTION                  AM_HAL_PIN_31_M3SCK
#define PIN_RADIO_SPI_MISO_FUNCTION                 AM_HAL_PIN_33_M3MISO
#define PIN_RADIO_SPI_MOSI_FUNCTION                 AM_HAL_PIN_32_M3MOSI
#define PIN_RADIO_SPI_CS_FUNCTION                   AM_HAL_PIN_24_NCE24
#define PIN_RADIO_SPI_CS2_FUNCTION                  AM_HAL_PIN_29_NCE29
#define PIN_RADIO_SPI_CS3_FUNCTION                  AM_HAL_PIN_25_NCE25

// IMU
#define IMU_I2C_NUMBER                              1
#define IMU_I2C_ADDRESS                             0x29
#define PIN_IMU_I2C_SCL                             8
#define PIN_IMU_I2C_SDA                             9
#define PIN_IMU_I2C_SCL_FUNCTION                    AM_HAL_PIN_8_M1SCL
#define PIN_IMU_I2C_SDA_FUNCTION                    AM_HAL_PIN_9_M1SDAWIR3
#define PIN_IMU_INTERRUPT                           17
#define PIN_IMU_RESET                               65

// LEDs
#define PIN_LED1_RED                                53
#define PIN_LED1_GREEN                              51

// Logging
#define PIN_SWO                                     3
#define PIN_SWO_FUNCTION                            AM_HAL_PIN_3_SWO

// Memory Storage (SPI)
#define STORAGE_SPI_NUMBER                          5
#define PIN_STORAGE_SPI_SCK                         47
#define PIN_STORAGE_SPI_MISO                        49
#define PIN_STORAGE_SPI_MOSI                        48
#define PIN_STORAGE_SPI_CS                          69
#define PIN_STORAGE_SPI_SCK_FUNCTION                AM_HAL_PIN_47_M5SCK
#define PIN_STORAGE_SPI_MISO_FUNCTION               AM_HAL_PIN_49_M5MISO
#define PIN_STORAGE_SPI_MOSI_FUNCTION               AM_HAL_PIN_48_M5MOSI
#define PIN_STORAGE_SPI_CS_FUNCTION                 AM_HAL_PIN_69_NCE69
#define PIN_STORAGE_WRITE_PROTECT                   30
#define PIN_STORAGE_HOLD                            6
#define MEMORY_PAGE_SIZE_BYTES                      2048
#define MEMORY_BLOCK_COUNT                          1024
#define MEMORY_ECC_BYTES_PER_PAGE                   64
#define STORAGE_DEVICE_ID                           { 0xEF, 0xBA, 0x21 }

// Timers
#define BUZZER_TIMER_NUMBER                         0
#define RADIO_WAKEUP_TIMER_NUMBER                   2
#define RADIO_WAKEUP_TIMER_TICK_RATE_HZ             (AM_HAL_CLKGEN_FREQ_MAX_HZ / 16)
#define BLE_SCANNING_TIMER_NUMBER                   3
#define BLE_SCANNING_TIMER_TICK_RATE_HZ             (AM_HAL_CLKGEN_FREQ_MAX_HZ / 16)

#endif  // #ifndef __PINOUT_HEADER_H__

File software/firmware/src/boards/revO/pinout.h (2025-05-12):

#ifndef __PINOUT_HEADER_H__
#define __PINOUT_HEADER_H__

// Hardware Revision ID
#include "revisions.h"
#define REVISION_ID                                 REVISION_O

// Battery
#define PIN_BATTERY_VOLTAGE                         18
#define PIN_BATTERY_VOLTAGE_FUNCTION                AM_HAL_PIN_18_ADCSE1
#define PIN_BATTERY_VOLTAGE_ADC_CHANNEL             AM_HAL_ADC_SLOT_CHSEL_SE1
#define PIN_BATTERY_CHARGING_STATUS                 58
#define PIN_BATTERY_INPUT_POWER_GOOD                60
#define PIN_BATTERY_CHARGE_COMPLETE_SIGNAL          66
#define VOLTAGE_DIVIDER_LOWER                       187
#define VOLTAGE_DIVIDER_UPPER                       510

// Buzzer
#define PIN_BUZZER_DRIVER                           55

// DecaWave Radio
#define RADIO_SPI_NUMBER                            1
#define PIN_RADIO_SPI_SCK                           8
#define PIN_RADIO_SPI_MISO                          10
#define PIN_RADIO_SPI_MOSI                          9
#define PIN_RADIO_SPI_CS                            14
#define PIN_RADIO_INTERRUPT                         27
#define PIN_RADIO_RESET                             50
#define PIN_RADIO_WAKEUP                            26
#define PIN_RADIO_ANTENNA_SELECT1                   24
#define PIN_RADIO_ANTENNA_SELECT2                   25
#define PIN_RADIO_SPI_SCK_FUNCTION                  AM_HAL_PIN_8_M1SCK
#define PIN_RADIO_SPI_MISO_FUNCTION                 AM_HAL_PIN_10_M1MISO
#define PIN_RADIO_SPI_MOSI_FUNCTION                 AM_HAL_PIN_9_M1MOSI
#define PIN_RADIO_SPI_CS_FUNCTION                   AM_HAL_PIN_14_NCE14

// IMU
#define IMU_SPI_NUMBER                              3
#define PIN_IMU_SPI_SCK                             31
#define PIN_IMU_SPI_MISO                            33
#define PIN_IMU_SPI_MOSI                            32
#define PIN_IMU_SPI_CS                              72
#define PIN_IMU_SPI_SCK_FUNCTION                    AM_HAL_PIN_31_M3SCK
#define PIN_IMU_SPI_MISO_FUNCTION                   AM_HAL_PIN_33_M3MISO
#define PIN_IMU_SPI_MOSI_FUNCTION                   AM_HAL_PIN_32_M3MOSI
#define PIN_IMU_SPI_CS_FUNCTION                     AM_HAL_PIN_72_NCE72
#define PIN_IMU_INTERRUPT                           17
#define PIN_IMU_RESET                               65
#define PIN_IMU_BOOT                                13
#define PIN_IMU_WAKEUP                              63

// LEDs
#define PIN_LED1_RED                                53
#define PIN_LED1_GREEN                              51
#define PIN_LED2_YELLOW                             79
#define PIN_LED2_RED                                88

// Logging
#define PIN_SWO                                     3
#define PIN_SWO_FUNCTION                            AM_HAL_PIN_3_SWO

// Storage
#define STORAGE_SPI_NUMBER                          5
#define PIN_STORAGE_SPI_SCK                         47
#define PIN_STORAGE_SPI_MISO                        49
#define PIN_STORAGE_SPI_MOSI                        48
#define PIN_STORAGE_SPI_CS                          69
#define PIN_STORAGE_SPI_SCK_FUNCTION                AM_HAL_PIN_47_M5SCK
#define PIN_STORAGE_SPI_MISO_FUNCTION               AM_HAL_PIN_49_M5MISO
#define PIN_STORAGE_SPI_MOSI_FUNCTION               AM_HAL_PIN_48_M5MOSI
#define PIN_STORAGE_SPI_CS_FUNCTION                 AM_HAL_PIN_69_NCE69
#define PIN_STORAGE_WRITE_PROTECT                   30
#define PIN_STORAGE_HOLD                            6
#define MEMORY_PAGE_SIZE_BYTES                      4096
#define MEMORY_BLOCK_COUNT                          4096
#define MEMORY_ECC_BYTES_PER_PAGE                   256
#define STORAGE_DEVICE_ID                           { 0x8D }

// Timers
#define BUZZER_TIMER_NUMBER                         0
#define RADIO_WAKEUP_TIMER_NUMBER                   2
#define RADIO_WAKEUP_TIMER_TICK_RATE_HZ             (AM_HAL_CLKGEN_FREQ_MAX_HZ / 16)
#define BLE_SCANNING_TIMER_NUMBER                   3
#define BLE_SCANNING_TIMER_TICK_RATE_HZ             (AM_HAL_CLKGEN_FREQ_MAX_HZ / 16)

// USB
#define PIN_USB_ENABLE1                             78
#define PIN_USB_ENABLE2                             81
#define PIN_USB_DETECT                              80

#endif  // #ifndef __PINOUT_HEADER_H__

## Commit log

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2018-07-02 added rev-c for the TriTag board
    [tritag.brd, tritag.sch, tritag_bom.csv, tritag_bom.xlsx]
2018-07-03 add EAGLE files for TriPoint v3
    [tripoint.brd, tripoint.sch, tritag.sch]
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2018-07-13 corrected decoupling cap values, added correct res for DEEPSLEEP plus missing decoupling caps
    [tripoint.brd, tripoint.sch]
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2018-07-18 added correct RF traces and board thickness
    [tripoint.brd]
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2018-07-21 added clearance for screws, decoupled FT232 to reduce power draw, added power planes
    [tritag.brd, tritag.sch]
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2018-07-23 changed polygons with too small width to 4mil / 1mil for silk
    [tritag.brd]
2018-07-24 added small fixes from Gerber inspection
    [tritag.brd]
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2018-07-24 adjusted files in BOM for voltage tolerance
    [tritag_bom.csv, tritag_bom.xlsx]
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2018-08-09 fixed silk screen, increased space between 0201 capacitors
    [tripoint.brd, tripoint.sch]
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2018-08-10 fixed open issues for rev D; added test pads for SPI bus, added VBAT to analog pin
    [tottag.brd, tottag.sch]
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2019-04-30 added battery, fixed RTC passives
    [tottag.brd, tottag.sch]
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2019-07-07 Replace obsolete power regulator
    [tottag.brd, tottag.sch]
2019-07-07 rev f cleanups
    - Fix footprint error in new regulator
    - Better shielding between 1.8V and debug signals
    - Better routing for `REG_EN` line
    - Clean up ground plane odditites
    - Remove vias from under RTC battery
    [tottag.brd, tottag.sch]
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2019-07-16 fix capacitor, resistor numbering
    [tottag.brd, tottag.sch]
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2019-07-17 fix BOM to add missing crystal (!)
    [tottag_bom.csv, tottag_bom.xlsx]
2019-07-18 rev_f: more BOM fixes
    - Remove duplicate C20 entry
    - Add B1 as DNP entry
    - C71 and C72, while both 10uF, are 0402 and 0603 packages :/
    [tottag_bom.csv, tottag_bom.xlsx]
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2020-05-30 rev_g: SD card SPI pullups 10k -> 100k
    To reduce leakage through the SD Card, increase the pullups on the SPI lines
    from 10k to 100k. This now matches the pullup already in use for the card
    present detection.
    Resistors renumbered as a result:
    > R16 : 10k 0402_RES => R13 : 10k 0402_RES
    > R17 : 10k 0402_RES => R14 : 10k 0402_RES
    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
    [tottag.brd, tottag.sch]
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2020-06-02 rev_g: [WIP] correct principle width to fit case
    Accidentally measured the distance between the *tips* of the PCB standoff
    and the case screw shaft, which added 3mm in Z. The standoff and screw should
    only be 8mm apart, not 11mm. With the extra 3mm, the corners of the board
    were clipping into the rounded corners of the case.
    [tottag.brd]
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2020-06-02 rev_g: [WIP] routing; fix power switch point
    Don't want to be in a situation where it's possible for the battery
    to not charge becuase the power switch is off. Instead of disconnecting
    the battery, disconnect the `VBAT` net from the regulator. Now if the
    switch is off, USB power won't work either, but that's an obvious fix
    that only happens in front of your face.
    [tottag.brd, tottag.sch]
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2020-06-04 rev_g: fix RTC supply to power from +3v3 not VCC
    There is no VCC net on tottag :(
    [tottag.brd, tottag.sch]
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2020-06-04 rev_g: documentation fixes
    - Add link in sch to battery test report
    - Delete superfluous `J4` label
    [tottag.brd, tottag.sch]
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2020-06-06 rev_g: replace SD with part with 3d model
    [tottag.brd, tottag.sch]
2020-06-08 rev_g: replace RTC battery with 3d model component
    [tottag.brd, tottag.sch]
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2020-06-11 rev_g: Fix SD / crystal placing; power planes
    Hopefully a reaonsable final pass minus cosmetics
    [tottag.brd, tottag.sch]
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2020-06-11 rev_g: two qick silk fixes
    [tottag.brd]
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2020-06-16 rev_g: move USB-C connector back a touch to fit
    That, of course, is a taller connector than the old micro, so it
    brushes the edge of the case, fix.
    [tottag.brd, tottag.sch]
2020-06-16 rev_g: fix X2 3d model to silence collision warning
    [tottag.brd, tottag.sch]
2020-06-16 rev_g: fix 3d models for some parts
    Seems if z is exactly on the board, there can be rounding errors that
    cause false positives in interference analysis; bump them up a bit.
    [tottag.brd, tottag.sch]
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2020-06-16 rev_g: [sch] fix body diode on pfet
    That was really confusing. Looks like a copy paste error from the
    dual n-channel part :( :(.
    [tottag.sch]
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2020-06-17 rev_g: some cosmetic silk fixes
    [tottag.brd]
2020-06-18 rev_g: schematic fixes from Andreas
    [tottag.brd, tottag.sch]
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2020-06-23 rev_g: design review fixes
    - Unify `!AD_EN` naming
    - C75/C76 10µF -> 1µF
    - Add battery pack details
    - Add NTC math details
    - Clarify switch on power diagram
    [tottag.brd, tottag.sch]
2020-06-23 rev_g: correct thermistor prefix (R36 -> RT1)
    [tottag.brd, tottag.sch]
2020-06-23 rev_g: Fix R31, R32 series / parallel
    [tottag.brd, tottag.sch]
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2020-06-24 rev_g: [WIP] design review fixes, board file
    - cleanup angle on BATT_THERM
    - C60 -> P1 not P3; connect GND
    - C61: route 3v3 to filter through; GND back to P2
    - More GND around U6 IC
    - P1/P2 GND pours for U6
    - Re-route VQI out of U6 to go expressly through filter caps before plane
    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
    [tottag.brd]
2020-06-24 rev_g: [WIP] design review fixes
    - Replace battery pinheader with individual pieces (allows U4 move later)
    - Fix lost ground plane (?!)
    - Then isolate and stitch up wireless ground plane to primary ground plane
    - Move routing from layer 2 to 15 where trivial to do so
    - Clean up C15 / C26 / C58 caps
    - Separate SD card passives from DW cap bank
    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
    [tottag.brd, tottag.sch]
2020-06-24 rev_g: [WIP] design review fixes
    - add missing keepouts for bottom-left antenna
    - improve (increase) power connections around speaker parts
    [tottag.brd, tottag.sch]
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2020-06-25 rev_g: Update battery monitor divider
    - Swap R's and change range a touch to get a wider voltage range
    [tottag.brd, tottag.sch]
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2020-06-30 rev_g: [WIP] design review
    - Move C56 up to allow X3 to move right and shorten traces
    - Improve LDO / VBAT connection
    - Move ground via by R18 a bit (passed DRC before :shrug:)
    - Re-route VQI for better layer 16 plane
    - More stiching vias in wireless ground planes
    - Re-route QI-TS-CTRL to remove needless bends
    [tottag.brd]
2020-06-30 rev_g: [WIP] design review
    - Move supply power traces to 15 and signals to 16
    - Tighten layer 2 escape routing around NRF
    - Fix B1, A3 labels
    - Add switch ON/OFF labels to both sides
    - Delete SquarePoint version :)
    [tottag.brd]
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2020-06-30 rev_g: [WIP] design review
    - Fix names, date, rev indicator (surprisingly hard!)
    [tottag.brd]
2020-06-30 rev_g: [WIP] design review
    - Replace JP1 with part with silk ring
    [tottag.brd, tottag.sch]
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2020-06-30 rev_g: fixup airwire I missed in the cap via adding :(
    [tottag.brd, tottag.sch]
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2020-06-30 rev_g: fix gnd near bottom left antenna feed
    [tottag.brd]
2020-06-30 rev_g: small trace fixes; plane cleanups
    [tottag.brd]
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2020-09-03 Restructuring, significant rewrites and bug fixes
    [module_data.ods]
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2021-02-10 bug fixes, exception handling, edge cases
    [40-41-Diary.csv, 41-42-Diary.csv]
2021-02-10 bug fixes, reorganization
    [40-41-Diary.csv, Event-Mapping.csv]
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2021-02-15 rev_h: split SPI buses; replace coil
    Pin updates from SPI reconfiguration:
    SPI0 (Accelerometer)
    SCLK: P0.17
    MISO: P0.15
    MOSI: P0.13
    (INT, CS pins unchanged)
    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
    [tottag.brd, tottag.sch]
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2021-02-17 rev_h: tie !CHG LED to +3v3
    This means the LED won't power on to indicate charging if the device
    is switched off, but that's an uncommon case anyway. We may even end
    up just DNP'ing the CHG LED; it's of middling use; in which case an
    internal nRF pull-up can be used in place of this for the !CHG net.
    [tottag.brd, tottag.sch]
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2021-02-17 rev_h: fix labels on test points for bottom buses
    [tottag.brd]
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2021-02-19 rev_h: fix cap routing for magnetometer
    The VddIO pin was connected to the filter/decap network of Vdd,
    rather than directly to the Vdd plane as proscribed in the datasheet.
    [tottag.brd]
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2021-04-23 fixed undefined events
    [katediaryc.csv]
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2023-04-10 fix VR2 footprint; add BOM
    [rev_i_v127-BOM.csv, rev_i_v127.sch, rev_i_v166.brd]
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2024-01-19 rev-m: fix ON/OFF bottom silk
    [rev_m_v4.brd]
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2024-07-30 doc: remove old/now-wrong info; start new doc
    Lots more to do, but this is a minimal set of the critical bits
    for the project writ large and the hardware
    [backplate_hexagon.SLDPRT, backplate_hexagon.STL, polypoint_backplate_hexagon.STL, staff.SLDPRT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]
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2024-11-13 rev_n: manufacturing fixes
    - Fix U2 footprint
    - Add tCream for S4
    - Fix AP4/9DOF SPI/I2C mux mismatch with SJ's
    - Removes RX9 and RZ12
    - Rename solder jumpers as SJ#
    [rev_n v35.sch, rev_n_v73.brd]
2024-11-13 rev_n: manufacturing update
    - Fix mask, cream for pads on S2, S3
    [rev_n v36.sch, rev_n v75.brd]
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

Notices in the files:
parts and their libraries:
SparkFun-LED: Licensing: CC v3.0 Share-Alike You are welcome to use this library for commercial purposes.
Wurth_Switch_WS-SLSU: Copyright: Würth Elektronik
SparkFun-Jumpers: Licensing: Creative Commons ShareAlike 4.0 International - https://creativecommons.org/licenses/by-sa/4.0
